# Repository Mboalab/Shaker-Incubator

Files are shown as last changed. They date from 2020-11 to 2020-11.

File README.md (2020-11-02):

# Shaker-Incubator

MboaLab in Cameroon were awarded a $750 grant by the Build Free and Open Science Hardware Project led by Andre Chagas and supported by the Mozilla Foundation to build a low-cost, open-source incubator for microbiology. This shaker incubator was built in collaboration with [Beneficial Bio](https://beneficial.bio/) following future plans from Incubator project, to incorporate orbital shaking to increase aeration of cultures and therefore the yield of micro-organisms and their products like proteins.  

**Why a Shaker-incubator?**
Most biology labs in Cameroon and elsewhere in resource-constrained contexts are under-equipped due to the high cost of lab equipment and it is essential for many protocols including open enzyme manufacturing to provide optimal conditions for cell growth, where some type of agitation or shaking is necessary to incorporate oxygen and evenly distribute nutrients throughout the culture media. That's often done by placing a separate shaker inside an incubator, but incubator shakers combine those functions for a more convenient and efficient setup. The incubator shaker can be used for growth of just about any kind of cell including bacterial cultures, tissue cultures, and yeast. 

**Why open hardware?**
We believe that DIY and Open Science Hardware can facilitate access to low-cost and high-quality equipment for biology labs in Cameroon, Ghana and beyond. 

All resources are openly licensed and linked below.

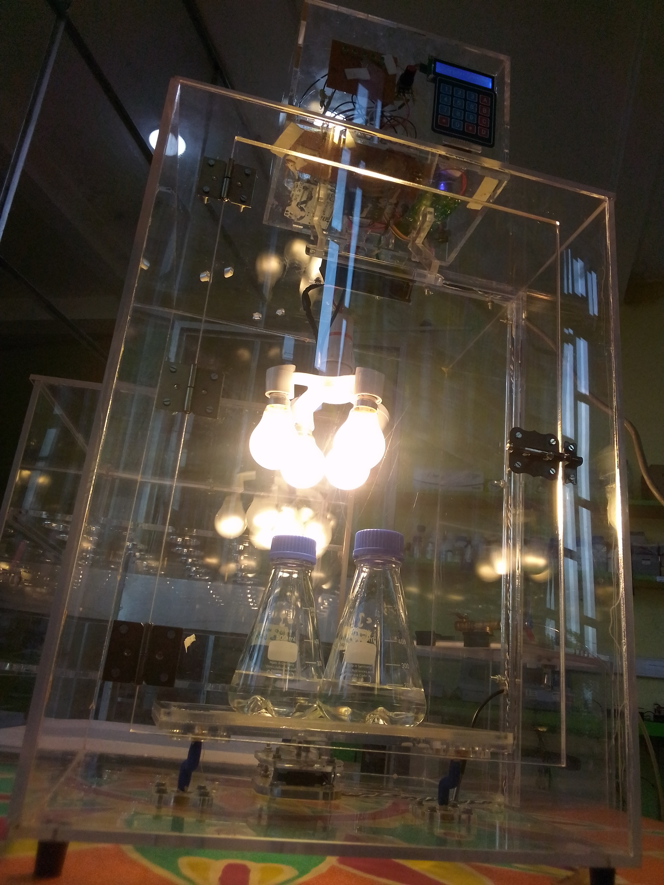
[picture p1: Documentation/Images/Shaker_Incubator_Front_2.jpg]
Shaker incubator frontview


# Build you own incubator

 - If you would like to build the device, get started by following the [build documentation](https://github.com/Mboalab/Shaker-Incubator/blob/main/Documentation/Building/Building.md)
 - The folders in this repository contain details of the [materials needed](https://github.com/Mboalab/Shaker-Incubator/blob/main/Hardware/BOM/BOM.md), laser cut design [files](https://github.com/Mboalab/Shaker-Incubator/tree/main/Hardware/Laser_Cut_Files), the Arduino-based [electronics design](https://github.com/Mboalab/Shaker-Incubator/tree/main/Hardware/Electronics) and firmware.
 - If you have questions or suggestions for improvements, please [add an issue](https://github.com/Mboalab/Shaker-Incubator/issues) or make a pull request.

# Related Links
[Beneficial Bio: ensuring the future of biomanufacturing is for the many and not the few](https://beneficial.bio/blogs/blog/beneficial-bio-ensuring-the-future-of-biomanufacturing-is-for-the-many-and-not-the-few)

# Acknowledgements

-   OPGES: Ariel Kameni
-   Image credits for Incubator: MboaLab Team

# Licensing

This hardware is licensed under [GNU General Public License v3.0](https://github.com/Mboalab/Shaker-Incubator/blob/main/License.md)

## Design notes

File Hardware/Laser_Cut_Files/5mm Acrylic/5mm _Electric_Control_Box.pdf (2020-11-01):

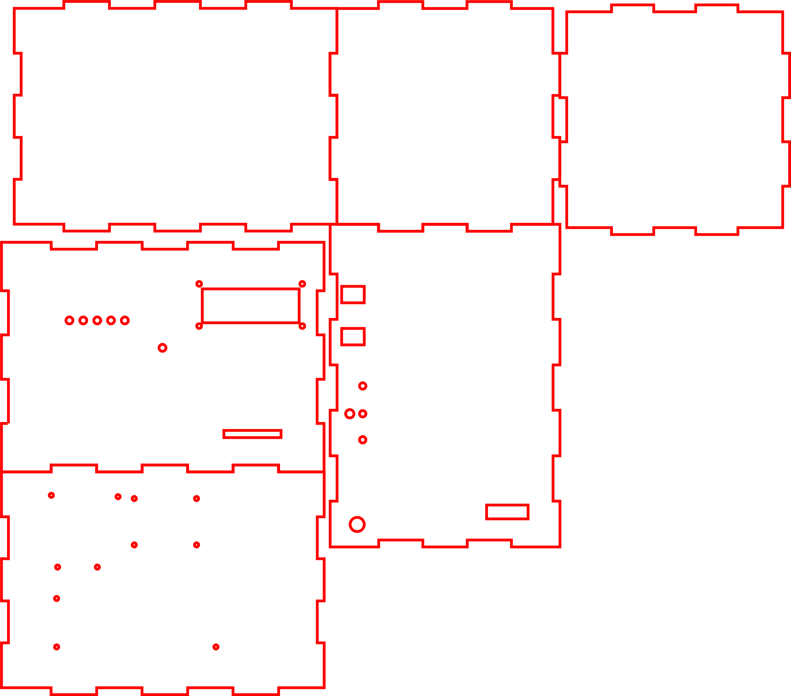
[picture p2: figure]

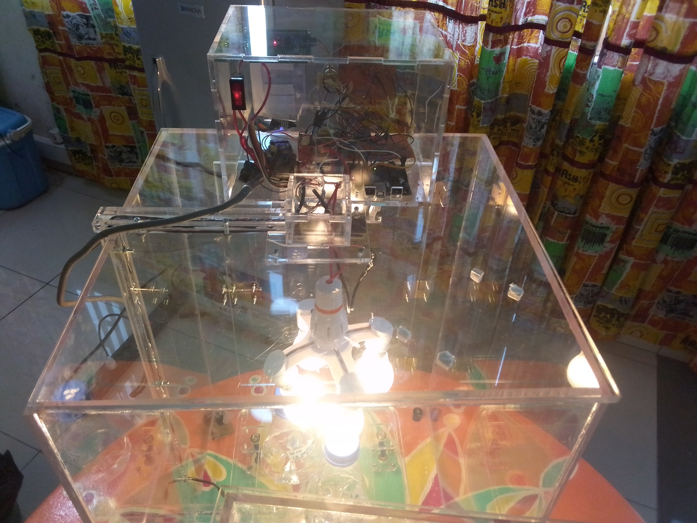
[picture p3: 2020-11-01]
Documentation/Images/Shaker_Incubator_Top.jpg

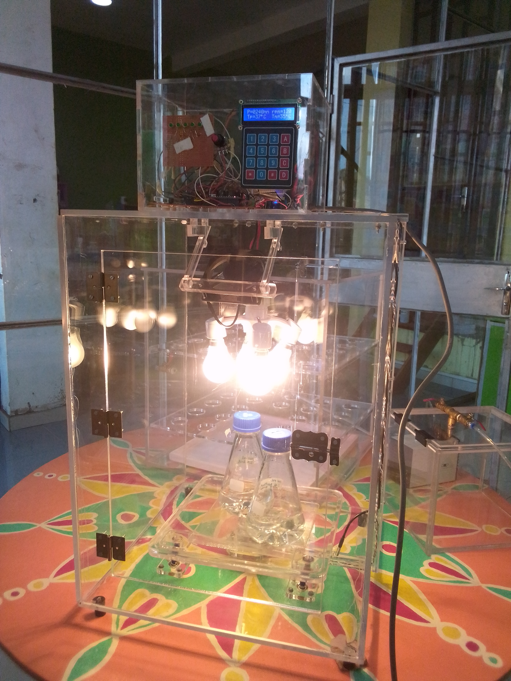
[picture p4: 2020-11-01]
Documentation/Images/Shaker_Incubator_Front_1.jpg

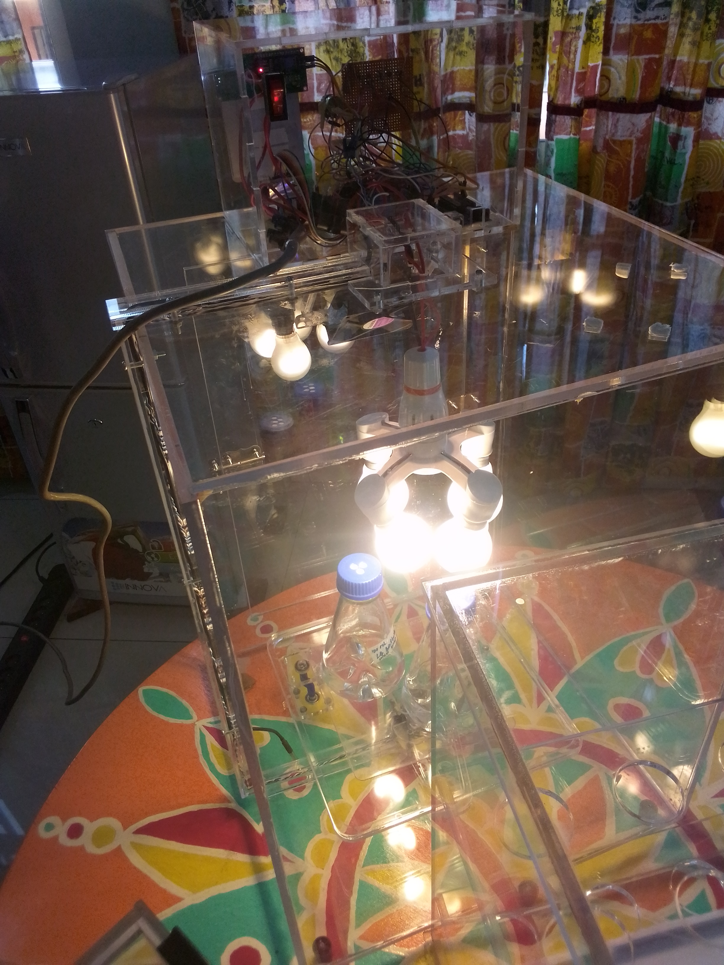
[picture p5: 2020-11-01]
Documentation/Images/Shaker_Incubator_Back.jpg

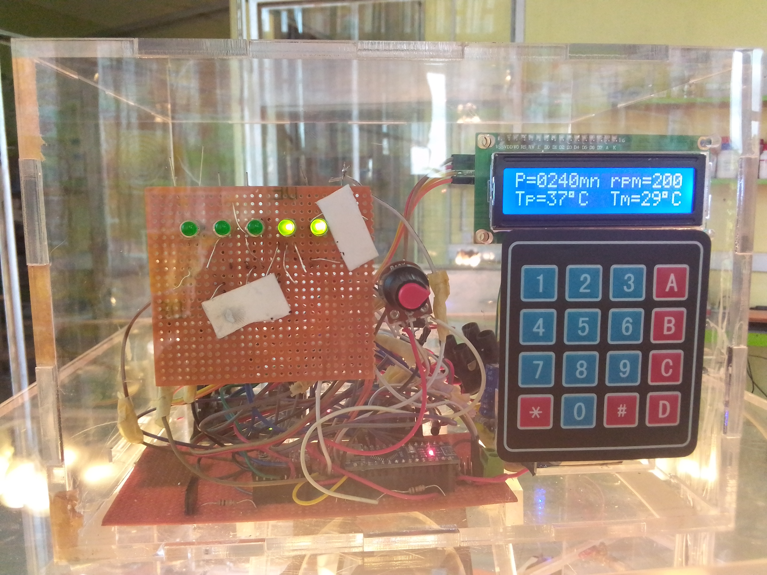
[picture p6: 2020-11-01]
Documentation/Images/Shaker_Incubator_LCD_Display.jpg

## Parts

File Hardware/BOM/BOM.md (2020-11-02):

## Electronics and Hardware
| N° | Amount | Description                 | Local supplier   | Cost (F CFA) | Datasheet |
|----|--------|-----------------            |------------------|--------------|--------------|
| 1  | 1      | Arduino Uno                 | [DBL Electronique](https://maps.app.goo.gl/5ZiqXomu7RbgKoKo7)| 7000         | [Datasheet](https://github.com/FOSH-following-demand/Incubator/blob/master/hardware/datasheets/Arduino_Uno.pdf) |
| 2  | 1      | 1602 LCD Display Module     | DBL Electronique | 3000         | [Datasheet](https://github.com/FOSH-following-demand/Incubator/blob/master/hardware/datasheets/1602A.pdf)|
| 3  | 1      | I2C                         | DBL Electronique | 1500         |           |
| 4  | 1      | Relay                       | DBL Electronique | 1000         |           |
| 5  | 1      | Temperature Sensor 18B20                  | DBL Electronique | 3500         | [Datasheet](https://github.com/FOSH-following-demand/Incubator/blob/master/hardware/datasheets/DS18B20.pdf)|
| 6  | 1      | USB cable A to B            | DBL Electronique | 1000         |           |
| 7  | 10     | Jumper Wires (Male to Male) | DBL Electronique | 500          |           |
| 8  | 10     | Jumper Wires (Male to Female) | DBL Electronique | 500          |          |
| 9  | 1      | Driver A4988              | DBL Electronique | 2500         |           |
| 10 | 1      | Potentiometer 10k (rotary)           | DBL Electronique | 250         |           |
| 11 | 1      | ON/Off Red LED Light illuminated Rocker Switch    | DBL Electronique | 1000         |          |
| 10 | 1(m)   | H05 V-K cable (0.50 mm²; 0.7 mm²…)                | DBL Electronique | 1000         |          |
| 10 | 1      | Power Supply Adapter AC to DC 220V To 12V                | DBL Electronique | 5000  |          |
| 10 | 10     | Resistor 1k              | DBL Electronique | 1500         |           |
| 10 | 3(m)   | Unshielded twisted pair (UTP) cables                  | DBL Electronique | 3000     |          |
| 10 | 2(m)   | Electric cable (4mm2)                  | DBL Electronique | 1000         |          |
| 10 | 2      | Breadboard                  | DBL Electronique | 3000         |           |
| 10 | 4      | Standard 5mm Green LED                 | DBL Electronique | 800         |         |
| 11 | 4      | Incandescent bulb (100W)*          | Hardware store   |2000           |           |
| 12 | 1      | Light Bulb Holder (simple)         | Hardware stores  |500           |            |
| 12 | 1      | Light Bulb Holder (Multiple:4)     | Hardware stores  |500           |            |
| 13 | 1      | Luster terminal (6mm2)                  | Local Markets    | 400      |           |
| 14 | 1      | Luster terminal (4mm2)                | Local Markets    | 200      |      |
| 14 | 1      | DC 12V 3.5 INCHES Cooling Fan                | Local Markets    | 3000      |      |
| 14 | 1      | Stepper Motor, Bipolar 1.7A 40Ncm (56.2oz.in) 40mm Body 4-Lead W/ 40mm Cable               | Local Markets    | 15000      |      |
| 14 | 33     | Screw nut systems (⌀4mm; H-2cm )                | Local Markets    | 9900     |      |
| 14 | 7      | Screw nut systems (⌀4mm; H-3cm )              | Local Markets    | 2100     |      |
| 14 | 12     | Screw nut systems (⌀3mm; H-3cm )                | Local Markets    | 3600     |      |
| 14 | 3      | Hinges 40x40                | Local Markets    | 1500     |      |
| 14 | 1      | Bolt latches (50mm)                | Local Markets    | 1000     |      |
| 14 | 10     | 7mm Deep Groove Ball Bearing (No. 607ZZ)                | Local Markets    | 10000     |      |
| 15 | 1      | 8 mm transparent acrylic* | Local Markets| 175000  |         |
| 15 | 1      | 5 mm transparent acrylic* | Local Markets| 15000  |         |
| 15 | 1      | Acrylic glue | Local Markets| 12000  |         |
| 15 | 1      | Acrylic laser cut | Local Fabalab| 28000  |         |
| 15 | 3      | Printing Eccentric rod (Type I) | 3D printing center| 3000  |         |
| 15 | 1      | Printing Eccentric rod (Type II) | 3D printing center| 2000  |         |
* The lightbulb could be replaced with another heater e.g. a PCB heater element or a Peltier element
* It's more suitable to use colored acrylic

## Mechanical

- Laser Cutter 
- Electric drill

## Tools

- Soldering kit
- Double-sided tape
- Digital multimeter

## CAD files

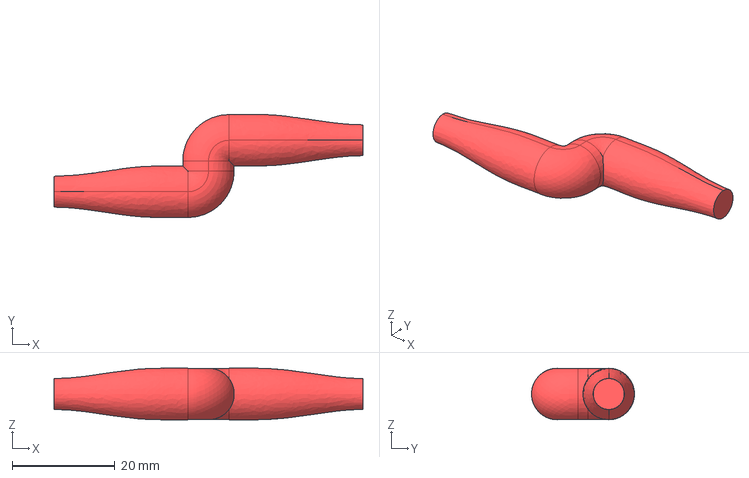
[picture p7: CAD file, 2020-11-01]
Hardware/3D files/Excentric_Rod_ Type 1.step
60.0 x 20.0 x 10.0 mm

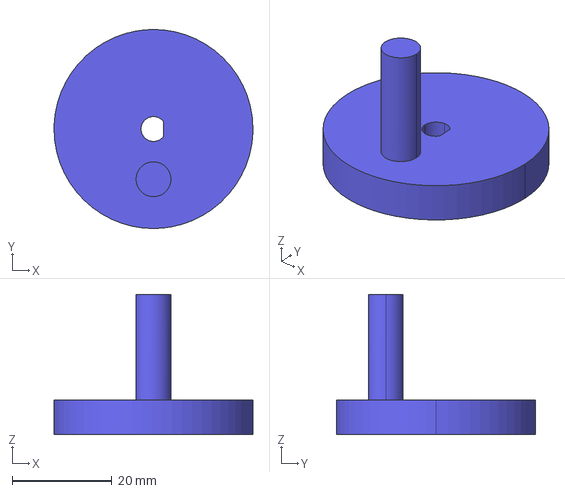
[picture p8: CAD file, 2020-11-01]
Hardware/3D files/Excentric_Rod_ type 2.step
40.0 x 40.0 x 28.2 mm

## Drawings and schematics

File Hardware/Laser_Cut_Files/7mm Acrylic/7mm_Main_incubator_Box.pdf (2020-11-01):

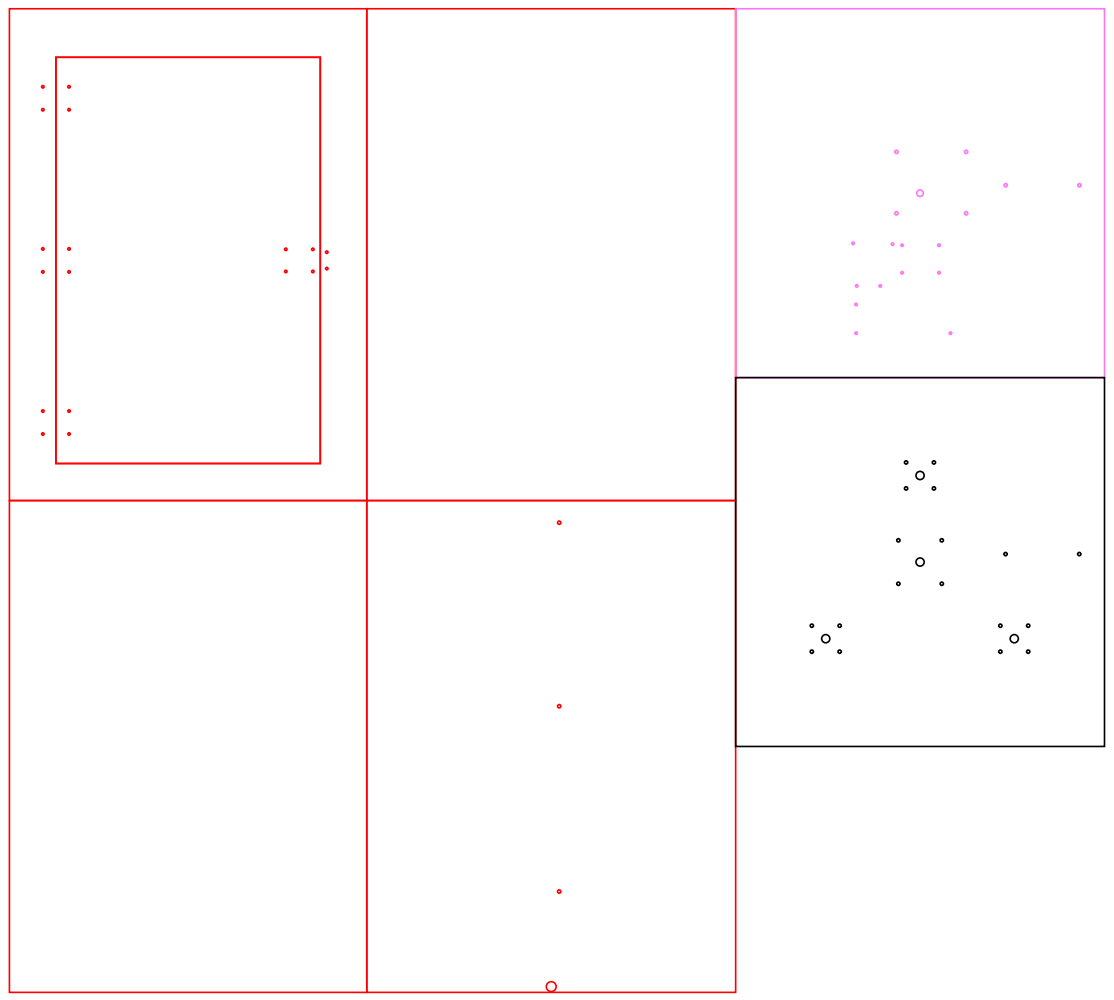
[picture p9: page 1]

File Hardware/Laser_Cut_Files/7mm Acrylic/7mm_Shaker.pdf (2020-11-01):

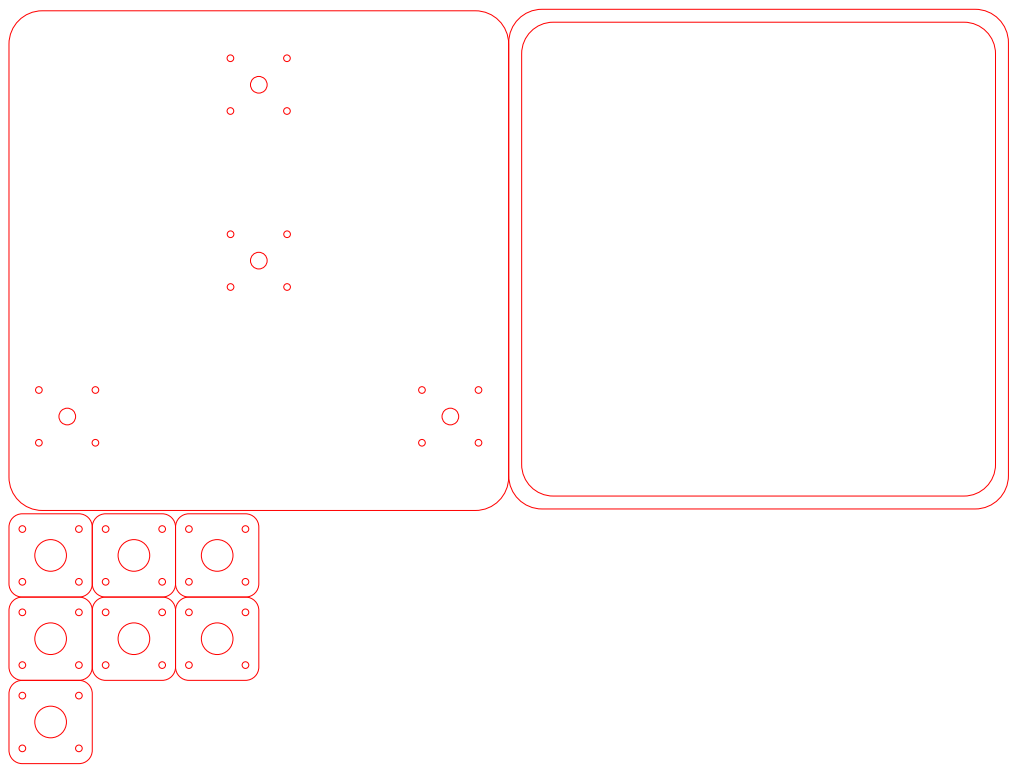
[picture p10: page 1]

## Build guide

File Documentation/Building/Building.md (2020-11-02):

## Getting started with assembly

This equipment is a shaker-incubator, designed to keep the contents at a constant temperature above the ambient temperature while providing agitation (orbital shaking). The shaker incubator is made up of 4 (four) main parts: 
**The electronic control box** : Centralizing the command and control of shaker’s speed as well as Incubation time and temperature;
**The shaker module**(oscillating board): embeded in acrylic box and providing shaking surface ; 
**The heat source**: Enabling fast generation and incrementation of heat within the incubator;
**The fan**: Enabling rapid and even distribution of heat within the incubator.

It is an insulated box (8mm acrylic glass) that contains a heater (lightbulb), a temperature sensor and some electronics and software that will control the temperature to keep it constant and also o adjust the speed of the oscillating board at the level input by the user. 

The primary use case is microbiology. It is essential for many protocols to have optimal growth temperature and for important microrganisms such as _Escherichia coli_ bacteria. However, most biology labs in Cameroon and elsewhere in resource-constrained contexts are under-equipped due to the high cost of lab equipment. Other use cases include washing blots, general mixing of solution and drying chamber.

To build the device you will need to undertake some basic soldering and load software onto an Arduino Uno microcontroller but you do not need to have prior experience as there are many tutorials and guides online. This build could be completed by one person in less than a week with all materials and facilities available.

If you have questions you can contact [@LabMboa](https://twitter.com/labmboa?lang=en) on Twitter or send an email to [Mboalab CMR](mboalab@gmail.com)

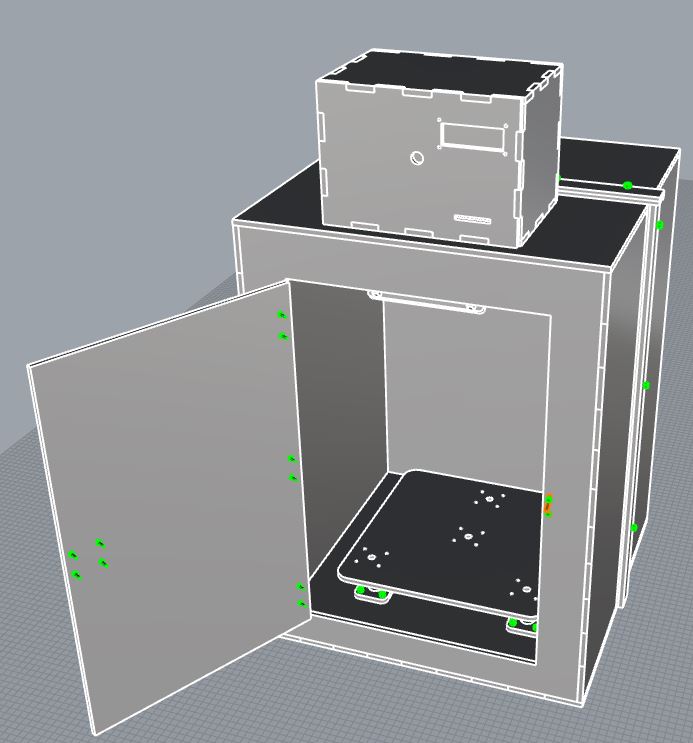
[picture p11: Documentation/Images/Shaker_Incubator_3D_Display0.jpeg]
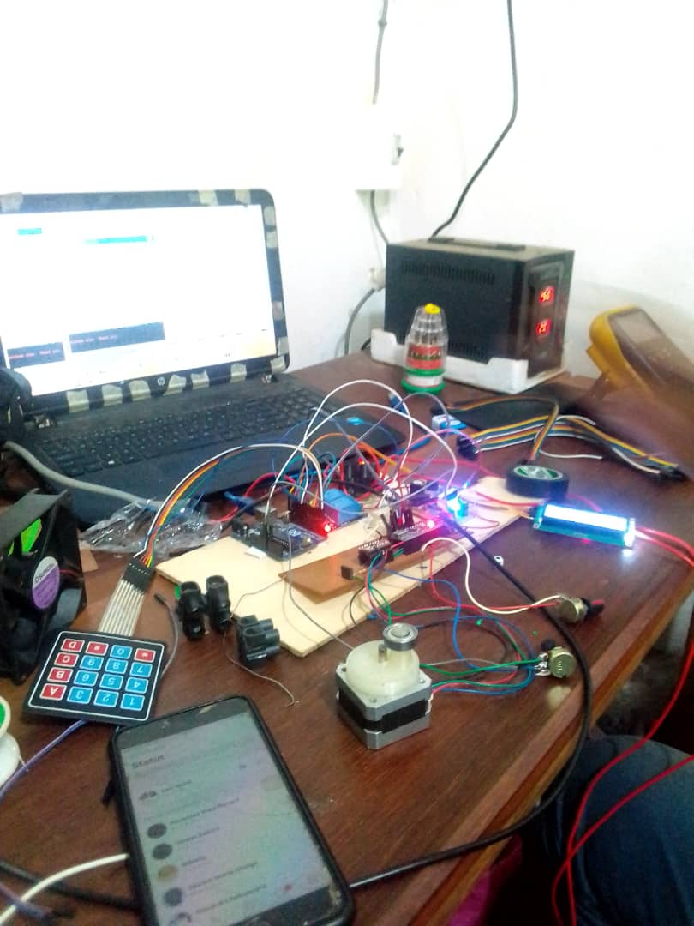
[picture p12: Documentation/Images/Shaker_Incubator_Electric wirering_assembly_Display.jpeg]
   
<br>

## Gathering your materials

The list of components and tools required can be found in the [Bill of Materials](https://github.com/Mboalab/Shaker-Incubator/blob/main/Hardware/BOM/BOM.md). 

<br>

## Build Steps

### Printing 3D parts and Laser cutting

### Assembling and testing the electronics

### Constructing the incubator box

### Constructing the electronics enclosure

### Integrating the electronics with the cooler box

### Mounting the shaker

### Checking that it works

 - Use a separate thermometer to verify that the temperature is reaching the correct point and is maintained.

Note: 

*3D files were generated with the software Rhino 3D version 6. Design files are opening with Rhino software.
Laser cutting files were generated with the software Inkscape.*

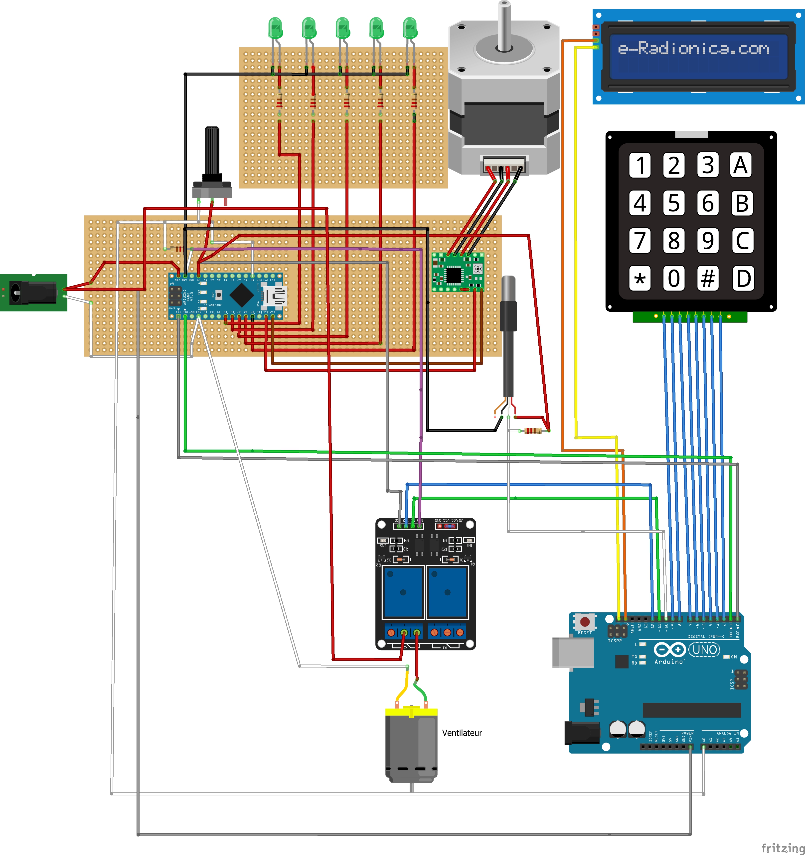
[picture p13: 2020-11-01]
Hardware/Electronics/Shaker_incubator_Wiring_Diagram_bb (1).jpg

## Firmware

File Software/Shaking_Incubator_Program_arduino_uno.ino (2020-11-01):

#include <Wire.h>
#include <LiquidCrystal_I2C.h>
#include <Keypad.h>
#include<EEPROM.h>
#include <OneWire.h>
#define turnOn 13
#define fan 12
#define bulb 11
OneWire  ds(10);  // on pin 10 (a 4.7K resistor is necessary)
const byte ROWS = 4; //four rows
const byte COLS = 4; //three columns
char keys[ROWS][COLS] = {
  {'1', '2', '3', 'A'},
  {'4', '5', '6', 'B'},
  {'7', '8', '9', 'C'},
  {'*', '0', '#', 'D'}
};
LiquidCrystal_I2C lcd(0x27, 20, 4); // set the LCD address to 0x27 for a 16 chars and 2 line display
byte rowPins[ROWS] = {9, 8, 7, 6}; //connect to the row pinouts of the keypad
byte colPins[COLS] = {5, 4, 3, 2};
Keypad keypad = Keypad( makeKeymap(keys), rowPins, colPins, ROWS, COLS );
int T_max = 1440;
int T = 1204;

char c_time[5] = {'.', '.', '.', '.', '\0'};
char ac_time[5] = {'.', '.', '.', '.', '\0'};
char c_temp[3] = {'.', '.', '\0'};
char ac_temp[3] = {'.', '.', '\0'};
long temps_restant = 0;
long temps_prog = 0;
float Tmin = 20;
float Tmax = 80;
long temps_ecoule = 0;
long atemps_restant = 0;
long t_1 = 0;
long prev = 0;
long prev_pre = 0;
int sensorValue = 0;
long temps_prog_eeprom = 0;
long temps_ecoule_eeprom = 0;
int s = 0;
int Tp = 0;
int aTp = 0;
int Tm = 0;
int cc = 0;
int asser = 0;
int enc = 0;
int jeu = 0;
float rpm = 0.0;
float dd=0;
void setup() {
  Serial.begin(9600);
  //EEPROM.write(0,
  // put your setup code here, to run once:
  temps_prog_eeprom = Read_eeprom(0);
  temps_ecoule_eeprom = Read_eeprom(1);
  Tp = read_eeprom_temp();
  temps_prog = temps_prog_eeprom;
  Serial.print("prog=");
  Serial.print(temps_prog_eeprom);
  Serial.print("   ecoul=");
  Serial.println(temps_ecoule_eeprom);
  //temps_ecoule=temps_ecoule*60000;
  temps_restant = temps_prog - temps_ecoule_eeprom;
  lcd.init();
  lcd.init();
  lcd.backlight();
  lcd.setCursor(0, 0);
  lcd.print("P=");
  lcd.setCursor(2, 0);
  lcd.print(c_time);
  lcd.setCursor(6, 0);
  lcd.print("mn");
  pinMode(turnOn, OUTPUT);
  pinMode(fan, OUTPUT);
  pinMode(bulb, OUTPUT);
  start_shake(0);
  start_fan_bulb(0);
  Serial.print(60 * (float)1000000 / (float)(400 * map(analogRead(A0), 550, 1023, 600, 2000)));
  delay(6000);
}

void loop() {
  //temps_restant=temps_prog;
  Tm = Calcul_temp_celsius_M();
  affiche_temp_mes(Tm);
  prev = millis();

  long p_eeprom = millis();
  if (temps_restant > 0)
  {
    int cx = (((float)temps_ecoule_eeprom) / ((float)temps_prog_eeprom)) * 100;
    sensorValue = analogRead(A0);
    sensorValue = sensorValue - sensorValue % 60;
    rpm = N(sensorValue);
    affiche_rpm(rpm);
    if (jeu < 1)
    {
      Serial.write('*');
      jeu = jeu + 1;
    }
    if (Tm >= Tp)
    {
      start_fan_bulb(0);
      asser = 1;
    }
    else
    {
      start_fan_bulb(1);
      // Serial.write('*');
    }
  }

  //Tp=read_eeprom_temp();
  while (temps_restant > 0 && asser != 0)
  {
    asser = 1;
    s = 1;
    int mis_a_jour_led = 0;
    if (millis() - p_eeprom > 60000)
    {
      temps_prog_eeprom = temps_prog;
      temps_ecoule_eeprom = temps_ecoule_eeprom + millis() - p_eeprom;
      Save_eeprom(0, temps_prog_eeprom);
      Save_eeprom(1, temps_ecoule_eeprom);
      save_eeprom_temp(Tp);
      p_eeprom = millis();
      mis_a_jour_led = 1;
      // Serial.println(temps_ecoule_eeprom);
    }
    Tm = Calcul_temp_celsius_M();
    affiche_temp_mes(Tm);
    affiche_temp_prog(Tp);
    temps_ecoule = millis() - prev;
    temps_restant = temps_prog_eeprom - (temps_ecoule_eeprom);
    affiche(temps_prog / 60000);
    sensorValue = analogRead(A0);
    sensorValue = sensorValue - sensorValue % 60;
    rpm = N(sensorValue);
    affiche_rpm(rpm);
    cc = (((float)temps_ecoule_eeprom) / ((float)temps_prog_eeprom)) * 100;

    if (cc < 20)
    {
      Serial.write('0');
    }
    else if (cc < 40)
    {
      Serial.write('1');
    }
    else if (cc < 60)
    {
      Serial.write('2');
    }
    else if (cc < 80)
    {
      Serial.write('3');
    }
    else if (cc < 100)
    {
      Serial.write('4');
    }
    else if (cc < 120)
    {
      Serial.write('5');
    }

    start_shake(1);
    char z = keypad.getKey();
    if (z)
    {
      set_param(z);
    }
    if (Tm >= Tp)
    {
      start_fan_bulb(0);
    }
    else
    {
      start_fan_bulb(1);
    }
  }
  if (s == 1)
  {
    temps_ecoule_eeprom = temps_prog_eeprom;
    Save_eeprom(1, temps_ecoule_eeprom);
    asser = 0;
    start_fan_bulb(0);
    s = 0;
  }

  start_shake(0);
  char z1 = keypad.getKey();
  if (z1)
  {
    set_param(z1);
  }
  affiche(temps_prog / 60000);
  affiche_temp_prog(Tp);
 sensorValue = analogRead(A0);
    sensorValue = sensorValue - sensorValue % 60;
    rpm = N(sensorValue);
    affiche_rpm(rpm);
  // affiche_rpm(60 * (float)1000000 / (float)(400 * map(analogRead(A0), 550, 1023, 600, 2000)));
}

void affiche_temp_mes(int x)
{
  lcd.setCursor(14, 1);
  lcd.write(0xDF);//Symbole du degre en hexadecimal. Correspondant a 223 en decimal
  lcd.setCursor(15, 1);
  lcd.print("C");
  lcd.setCursor(9, 1);
  lcd.print("Tm=");
  lcd.print(x);
}

void affiche_temp_prog(int x)
{
  lcd.setCursor(0, 1);
  lcd.print("Tp=");
  lcd.setCursor(5, 1);
  lcd.write(0xDF);//Symbole du degre en hexadecimal. Correspondant a 223 en decimal
  lcd.setCursor(6, 1);
  lcd.print("C");
  if (x >= 0 && x < 10)
  {
    lcd.setCursor(3, 1);
    lcd.print("0");
    lcd.setCursor(4, 1);
    lcd.print(x);
  }
  else if (x < 100)
  {
    lcd.setCursor(3, 1);
    lcd.print(x);
  }
}
void set_param(char c)
{
  if (c == 'A')
  {
    set_time('A');
  }
  else if (c == 'B')
  {
    set_temp('B');
  }
}
void set_temp(char c)
{

  int k = 0;
  char keye1 = keypad.getKey();
  keye1 = c;
  // put your main code here, to run repeatedly:

  // temps_restant= chiffr_saisi(c_time[0])*1000+chiffr_saisi(c_time[1])*100+chiffr_saisi(c_time[2])*10+chiffr_saisi(c_time[3]);
  // atemps_restant=temps_restant;
  if (keye1) {
    //Serial.println(keye);
    if (keye1 == 'B')
    {
      ac_temp[0] = c_temp[0];
      ac_temp[1] = c_temp[1];
      c_temp[0] = '0';
      c_temp[1] = '0';
      aTp = Tp;
      lcd.setCursor(3, 1);
      lcd.print(c_temp);
      lcd.setCursor(5, 1);
      lcd.print("  ");
      long previous = millis();
      char key1 = '\0';
      do
      {
        key1 = keypad.getKey();
        if (key1)
        {
          //Serial.println(key);
          if (chiffr_saisi(key1) <= 9)
          {
            lcd.setCursor(3, 1);
            if (k == 0)
            {
              previous = millis();
              c_temp[1] = key1;
              k = 1;
              lcd.print(c_temp);
            }
            else if (k == 1)
            {
              c_temp[0] = c_temp[1];
              c_temp[1] = key1;
              k = k + 1;
              lcd.print(c_temp);
              previous = millis();
            }
          }
          if (key1 == 'D')
          {
            c_temp[0] = '0';
            c_temp[1] = '0';
            lcd.setCursor(3, 1);
            lcd.print(c_temp);
            key1 = 0;
            k = 0;
          }
        }

      } while (millis() - previous < 20000 && key1 != '#');
      k = 0;
      if (key1 == '#')
      {
        //Serial.print(chiffr_saisi(key));
        Tp = chiffr_saisi(c_temp[0]) * 10 + chiffr_saisi(c_temp[1]);
        save_eeprom_temp(Tp);
        //affiche_temp_prog(Tp);
        ac_temp[0] = c_temp[0];
        ac_temp[1] = c_temp[1];
        k = 0;
      }
      else
      {
        c_temp[0] = ac_temp[0];
        c_temp[1] = ac_temp[1];
        Tp = aTp;
        affiche_temp_prog(Tp);
        k = 0;
      }
    }
  }
}
void set_time(char c)
{

  int k = 0;
  char keye1 = keypad.getKey();
  keye1 = c;
  // put your main code here, to run repeatedly:

  // temps_restant= chiffr_saisi(c_time[0])*1000+chiffr_saisi(c_time[1])*100+chiffr_saisi(c_time[2])*10+chiffr_saisi(c_time[3]);
  // atemps_restant=temps_restant;
  if (keye1) {
    //Serial.println(keye);
    if (keye1 == 'A')
    {
      ac_time[0] = c_time[0];
      ac_time[1] = c_time[1];
      ac_time[2] = c_time[2];
      ac_time[3] = c_time[3];
      c_time[0] = '0';
      c_time[1] = '0';
      c_time[2] = '0';
      c_time[3] = '0';
      atemps_restant = 60000 * (chiffr_saisi(ac_time[0]) * 1000 + chiffr_saisi(ac_time[1]) * 100 + chiffr_saisi(ac_time[2]) * 10 + chiffr_saisi(ac_time[3]));
      lcd.setCursor(2, 0);
      lcd.print(c_time);
      lcd.setCursor(6, 0);
      lcd.print("  ");
      long previous = millis();
      char key1 = '\0';
      do
      {
        key1 = keypad.getKey();
        if (key1)
        {
          //Serial.println(key);
          if (chiffr_saisi(key1) <= 9)
          {
            lcd.setCursor(2, 0);
            if (k == 0)
            {
              previous = millis();
              c_time[3] = key1;
              k = 1;
              lcd.print(c_time);
            }
            else if (k == 1)
            {
              c_time[2] = c_time[3];
              c_time[3] = key1;
              k = k + 1;
              lcd.print(c_time);
              previous = millis();
            }
            else if (k == 2)
            {
              c_time[1] = c_time[2];
              c_time[2] = c_time[3];
              c_time[3] = key1;
              k = 3;
              lcd.print(c_time);
              previous = millis();
            }
            else if (k == 3)
            {
              c_time[0] = c_time[1];
              c_time[1] = c_time[2];
              c_time[2] = c_time[3];
              c_time[3] = key1;
              k = 4;
              lcd.print(c_time);
              previous = millis();
            }
          }
          if (key1 == 'D')
          {
            c_time[0] = '0';
            c_time[1] = '0';
            c_time[2] = '0';
            c_time[3] = '0';
            lcd.setCursor(2, 0);
            lcd.print(c_time);
            key1 = 0;
            k = 0;
          }
        }

      } while (millis() - previous < 20000 && key1 != '#');
      k = 0;
      if (key1 == '#')
      {
        //Serial.print(chiffr_saisi(key));
        temps_prog = 60000 * (chiffr_saisi(c_time[0]) * 1000 + chiffr_saisi(c_time[1]) * 100 + chiffr_saisi(c_time[2]) * 10 + chiffr_saisi(c_time[3]));
        temps_restant = temps_prog;
        temps_ecoule = 0;
        temps_prog_eeprom = temps_prog;
        temps_ecoule_eeprom = temps_ecoule;
        Save_eeprom(0, temps_prog_eeprom);
        Save_eeprom(1, temps_ecoule_eeprom);
        affiche_rpm((((float)temps_ecoule_eeprom) / ((float)temps_prog_eeprom)) * 100);
        ac_time[0] = c_time[0];
        ac_time[1] = c_time[1];
        ac_time[2] = c_time[2];
        ac_time[3] = c_time[3];
        atemps_restant = temps_restant;
        lcd.setCursor(6, 0);
        lcd.print("mn");
        k = 0;
      }
      else
      {
        c_time[0] = ac_time[0];
        c_time[1] = ac_time[1];
        c_time[2] = ac_time[2];
        c_time[3] = ac_time[3];
        k = 0;
      }
    }
  }
}
void affiche(int Tm)
{
  lcd.setCursor(6, 0);
  lcd.print("mn");
  if (Tm >= 0 && Tm < 10)
  {
    lcd.setCursor(2, 0);
    lcd.print("000");
    lcd.setCursor(5, 0);
    lcd.print(Tm);
  }
  else if (Tm < 100)
  {
    lcd.setCursor(2, 0);
    lcd.print("00");
    lcd.setCursor(4, 0);
    lcd.print(Tm);
  }
  else if (Tm < 1000)
  {
    lcd.setCursor(2, 0);
    lcd.print("0");
    lcd.setCursor(3, 0);
    lcd.print(Tm);
  }
  else if (Tm < 10000)
  {
    lcd.setCursor(2, 0);
    lcd.print(Tm);
  }
}
int chiffr_saisi (char c)
{
  if (c == '0')
  {
    return 0;
  }
  else if (c == '1') return 1;
  else if (c == '2') return 2;
  else if (c == '3') return 3;
  else if (c == '4') return 4;
  else if (c == '5') return 5;
  else if (c == '6') return 6;
  else if (c == '7') return 7;
  else if (c == '8') return 8;
  else if (c == '9') return 9;
  else return 10;


}
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

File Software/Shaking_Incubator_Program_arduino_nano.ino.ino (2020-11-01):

/*Example sketch to control a stepper motor with A4988/DRV8825 stepper motor driver and Arduino without a library. More info: https://www.makerguides.com */

// Define stepper motor connections and steps per revolution:
#define dirPin 12
#define stepPin 11
#define enablepin 4
#define command_Mot 10
#define stepsPerRevolution 200
#define NOT_AN_INTERRUPT -1
#define motorInterfaceType 1
#define d 50
#include <Wire.h>
#include <LiquidCrystal_I2C.h>
#include <AccelStepper.h>
LiquidCrystal_I2C lcd(0x27, 16, 2);
// Create a new instance of the AccelStepper class:
//AccelStepper stepper = AccelStepper(motorInterfaceType, stepPin, dirPin);
int freq = 600;
int nb_int = 0;
void setup() {
  // Declare pins as output:
  lcd.init();                      // initialize the lcd
  lcd.init();
  lcd.backlight();
  // Set the speed in steps per second:
  // stepper.setMaxSpeed(3000);
  pinMode(stepPin, OUTPUT);
  pinMode(dirPin, OUTPUT);
  pinMode(enablepin, OUTPUT);
  pinMode(command_Mot, INPUT);
  pinMode(12, OUTPUT);
  pinMode(5, OUTPUT);
  pinMode(6, OUTPUT);
  pinMode(7, OUTPUT);
  pinMode(8, OUTPUT);
  pinMode(9, OUTPUT);
  lcd.clear();
  Serial.begin(9600);
  for (int a = 0; a < 5; a++)
  {
    jeu_de_led();
  }
  //  initialisation_interrupt();
}


int frq = 0;
int a = 0;
int b = 0;
int sensorValue = 0;
float rpm = 0;
float dd = 0;
void loop() {
  // Set the spinning direction clockwise:
  digitalWrite(dirPin, LOW);
  if (Serial.available())
  {

    char c = Serial.read();

    if (c == '0')
    {
      a = 1;
      digitalWrite(9, LOW);
      digitalWrite(8, LOW);
      digitalWrite(7, LOW);
      digitalWrite(6, LOW);
      digitalWrite(5, LOW);
    }
    else if (c == '1')
    {
      a = 1;
      digitalWrite(9, HIGH);
      digitalWrite(8, LOW);
      digitalWrite(7, LOW);
      digitalWrite(6, LOW);
      digitalWrite(5, LOW);
    }
    else if (c == '2')
    {
      a = 1;
      digitalWrite(9, HIGH);
      digitalWrite(8, HIGH);
      digitalWrite(7, LOW);
      digitalWrite(6, LOW);
      digitalWrite(5, LOW);
    }
    else if (c == '3')
    {
      a = 1;
      digitalWrite(9, HIGH);
      digitalWrite(8, HIGH);
      digitalWrite(7, HIGH);
      digitalWrite(6, LOW);
      digitalWrite(5, LOW);
    }
    else if (c == '4')
    {
      a = 1;
      digitalWrite(9, HIGH);
      digitalWrite(8, HIGH);
      digitalWrite(7, HIGH);
      digitalWrite(6, HIGH);
      digitalWrite(5, LOW);
    }
    else if (c == '5')
    {
      a = 1;
      digitalWrite(9, HIGH);
      digitalWrite(8, HIGH);
      digitalWrite(7, HIGH);
      digitalWrite(6, HIGH);
      digitalWrite(5, HIGH);
    }
    /*else if (c == '*')
      {
      jeu_de_led();
      }*/
  }
  else
  {
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
